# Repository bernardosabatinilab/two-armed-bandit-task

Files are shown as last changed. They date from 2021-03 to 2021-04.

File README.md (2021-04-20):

# two-armed-bandit-task

This is an experimental protcol designed within the Sabtini lab of a freely-moving two-armed-bandit task. These files will allow you to build the behavioral arena and begin running 2ABT in mice. 

Laser cutting plans to build the behavioral arena as well as 3D-printing files are located within the "laser cutter" folder. 
Printed Circuit Board (PCB) plans and code is available under the "Two-Armed-Bandit-PCB" repo forked from the Harvard Medical School Insrumentation Core https://github.com/bernardosabatinilab/Two-Armed-Bandit-PCB.
Aquisiton code to control the behavioral arena can be found in the "Mouse-Bandit-Behavior-markov" folder.

Please read "2ABT protocol" for details on behavioral training, learning criterion, and trouble shooting tips.

MATLAB and Arduino IDE is required.



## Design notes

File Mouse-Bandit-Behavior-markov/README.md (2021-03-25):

# two-armed-bandit-3PortNosePoke-behaviorCode
Code to run two-armed-bandit mouse behavior. Center port is initiation port, left and right ports are rewarded ports.

This code was developed by Shay Neufeld and Ofer Mazor

# Behavior Structure
Based on behavioral paradigm published in Tai & Lee et al. 2012 (http://www.ncbi.nlm.nih.gov/pmc/articles/PMC3951287/)

# What you need
Software Requirements:  
1. MATLAB (currently tested on 2015a and 2016a)  
2. Arduino (https://www.arduino.cc/en/Main/Software)  

Hardware Requirements:  
1. Arduino uno  
2. Custom circuit (please see Two-Armed-Bandit-PCB repo)  

Other materials:  
1. 3x IR beam detectors  
2. 3x nose ports  
3. box to contain mouse  
4. 3x LEDs  
5. Water delivery system (60ml syringe to hold water, various tubes, needle to deliver rewards, solenoids to drive water delivery).

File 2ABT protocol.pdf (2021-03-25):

Freely-Moving Two-Armed Bandit – Sabatini Lab
consolidated protocol from Lynne Chantranupong and Michael Wallace Habituation phase – 1 week prior to behavioral arena exposure
- Singly house mice, water deprived to 80% original body weight (BW)
- Handle mice for ~5 minutes/day
- Administer water by syringe during handling
- Place 1-1.5 mL of water in home cage to maintain water-restricted BW Pre-training/Daily setup – Configuring Arduino and data directory

### 1. Configure Arduino

a. Open Arduino IDE
b. Open MultiNoseportController
c. Compile and load onto Arduino board

### 2. Configure MATLAB

a. Add Mouse-Bandit-Behavior-markov folder to path
b. Run NewGUI in command window

### 3. Configure NewGUI – flush tubing

a. Select Connect to Arduino
b. Number of iterations = 100
c. Left/Right duration = 450 ms
d. Select Flush Left until all air bubbles are removed
e. Select Flush Right until all air bubbles are removed
f. Wipe away remaining water in ports

### 4. Running an experiment – choosing data directory

a. Define mouse name
b. Select: Choose Directory to Save In (select desired directory location)
c. Type in desired parameters in GUI
d. Select: Run Experiment

### 5. Stopping a session

a. Select: Stop Experiment
b. Clean box

Pre-training – behavioral arena setup/calibration
- Flush tubing with clean water by increasing solenoid valve opening time to 500 ms, 100 iterations on GUI.
- Change solenoid valve opening time to 50 ms, 1 iteration on GUI. Confirm that water delivery occurs in the form of a droplet.
- Calibrate ports (weekly) by:
1. Set solenoid opening time to 50 ms, 100 iterations
2. Aim for 300 uL of water to be dispensed during this time
3. Adjust solenoid opening time accordingly until both ports release 300 uL of water.

Training – 7-21 days
Day 1/Stage 1: Mice learn that water is available from side port lick spouts Bait center port and side ports with approximately 10 uL of water.
Weigh mouse then place in behavioral arena.
Set GUI parameters to:
Center poke trigger = 0
Center poke reward window = 0
Left/Right reward probability = 1/1
Min/Max block range: 1000
Learning criterion: train mice until they have reached a total of 150-200 rewarded trials then, proceed to next training stage.
Stage 2: Introduce trial structure – center to side nose poke for reward delivery
Bait lick spouts with 10 uL of water
Weigh mouse then place in behavioral arena
Session time = 40 min
Set GUI parameters to:
Center poke trigger: 15 s
Center poke reward window: 1
Left/Right reward probability: 1/1
Min/Max block range: 1000
Learning criterion: >100 correct trials/session; proceed to next training stage.
Stage 3: Learning block structure – rewarded trials switch sides with each block transition Bait center and rewarded ports with 10 uL of water.
Weigh mouse and place in behavioral arena.
Set GUI parameters to:
Center poke trigger: 15 s
Center poke reward window: 1
Left/Right reward probability: 1/0*
*Counterbalance rewarded side every session to minimize development of bias Min/Max block range: 30
Learning criterion: ~70% accuracy across 6 blocks; proceed to next training stage

Stage 4: Introduction of physical barrier between reward ports and initiation port

Note: A well-trained, experienced mouse can perform a single trial within 300-400 ms which is too fast to resolve a photometry signal for a single trial. Therefore, physical barriers are introduced to increase trial time.

Barriers reach a maximum length of 6 cm. These are introduced in a gradual, stepwise manner so that animals can adjust their movements to accommodate the barriers. Barriers begin at 1.5 cm in length then, increase to 3 cm then, finally to 6 cm.

Install appropriate barriers.
Bait center and rewarded ports with 10 uL of water.
*Note: Once mice achieve criterion on shortest barrier, stop baiting center port. Set GUI parameters to:
Center poke trigger: 15 s
Center poke reward window: 1
Left/Right reward probability: 1/0*
*Counterbalance rewarded side every session Min/Max block range: 30
Learning criterion: ~70% accuracy across 6 blocks then, can increase barrier length and/or move on to the final training stage.
Trouble shooting tips: If the mouse is struggling with the introduction of the barriers, change block range to 20 until mice perform well, bait rewarded port to help and place tape over unrewarded port if necessary. Then, increase block range to 30.

Stage 5: Final block structure for well-trained mice
Install longest barrier.
Bait rewarded ports with 10 uL of water.
Weigh mouse and place in behavioral arena.
Set GUI parameters to:
Center poke trigger: 5 s
Center poke reward window: 1 Left/Right reward probability: 0.9/0.1 Min/Max block range: 30

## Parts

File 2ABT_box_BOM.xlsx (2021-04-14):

Part | Type | Quantity | cost | total cost | Purpose | Notes | Link
noseport | box material | 3 |  | $0.00 | for poking | we can 3D-print these out here | see 3D printing files
#4-40 Cap screw | hardware | 1 | $10.00 | $10.00 | for box assembly | pre-thread holes for screws
Arduino UNO | hardware | 1 | $23.00 | $23.00 |  |  | https://www.arduino.cc/en/Main/ArduinoBoardUno
solenoid | electronics | 2 | $60.00 | $120.00 | for water delivery | LHQA0531220H (quiet click) | https://www.theleeco.com/products/electro-fluidic-systems/solenoid-valves/control-valves/lhq-series/3-port/ported/
LEDs | electronics | 3 | $10.00 | $30.00 | for lights |  | https://www.amazon.com/Emitting-Assortment-Diffused-Yellow-Colors/dp/B07DQQCXV9?hvadid=242051162351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
cables |  | 1 | $10.00 | $10.00 |  | Test Leads Breadboard 20 Pack 5.9 Inch (150mm) Wire Pin Contacts | http://www.jameco.com/webapp/wcs/stores/servlet/ProductDisplay?search_type=jamecoall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
IR beam detector | hardware | 3 | $6.46 | $19.38 | detect pokes |  | http://www.digikey.com/products/en?keywords=365-1769-ND
power source (5V) | electronics | 1 | $10.00 | $10.00 | for arduino |  | https://www.sparkfun.com/products/12889
Capacitive Touch Breakout | electronics | 3 | $6.00 | $18.00 | for lick detection |  | https://www.sparkfun.com/products/14520
60 mL syringes |  | 1 | $10.00 | $10.00 |  | water reservoir
tubing |  | 1 | $10.00 | $10.00 |  | Masterflex SC0040-LT Tygon E-Lab ext tubing, 1.42mm, 100ft | https://www.coleparmer.com/i/masterflex-sc0040-lt-tygon-e-lab-ext-tubing-1-42mm-100ft/0646034?searchterm=WU-06460-34
lick spouts |  | 1 | $10.00 | $10.00 |  |  | https://www.mcmaster.com/5560K72/
2AB printed circuit board | PCB | 1 |  | $0.00 |  | designed by Ofer Mazor, also includes parts list for screw terminals, ect. | https://github.com/HMS-RIC/Two-Armed-Bandit-PCB
Intel NUC NUC5i5RYK | computer | 1 | $1200.00 | $1200.00 | record data |  | https://www.amazon.com/Intel-NUC5i5RYK-Core-Processor-BOXNUC5I5RYK/dp/B00SD9ISIQ
Crucial 16GB Kit (8GBx2) DDR3-1600 MT/s (PC3-12800) 204-Pin SODIMM Notebook Memory CT2KIT102464BF160B / CT2CP102464BF160B | computer | 1 |  | $0.00 | record data |  | https://www.amazon.com/Crucial-DDR3-1600-PC3-12800-CT2KIT102464BF160B-CT2CP102464BF160B/dp/B007B5S52C
Samsung 850 EVO 500 GB M.2 3.5-Inch SSD (MZ-N5E500BW) | computer | 1 |  | $0.00 | record data |  | https://www.amazon.com/Samsung-850-EVO-3-5-Inch-MZ-N5E500BW/dp/B00TGIW1XG

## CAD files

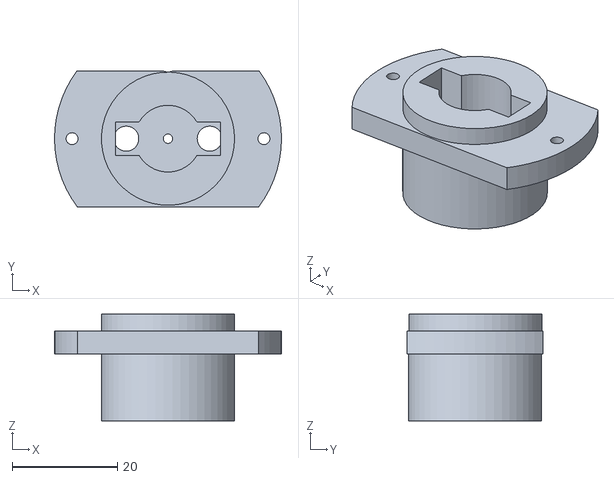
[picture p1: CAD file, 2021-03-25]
laser cutter/NosePokeBody.STL
43.2 x 25.8 x 20.3

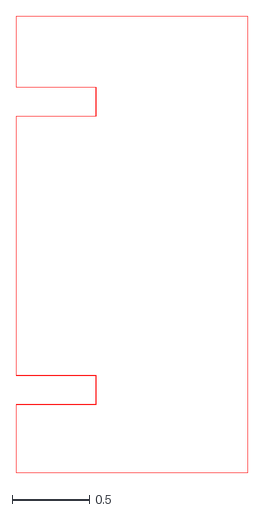
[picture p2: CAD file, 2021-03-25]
laser cutter/separation_holder.dxf
1.50 x 2.96

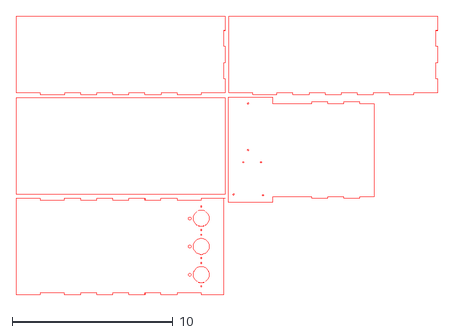
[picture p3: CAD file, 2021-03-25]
laser cutter/behavior box _small.dxf
26.2 x 17.3

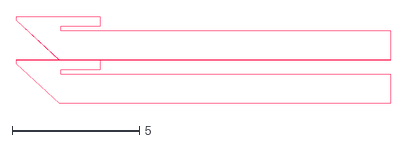
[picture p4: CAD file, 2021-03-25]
laser cutter/dividers_short.dxf
14.7 x 3.42

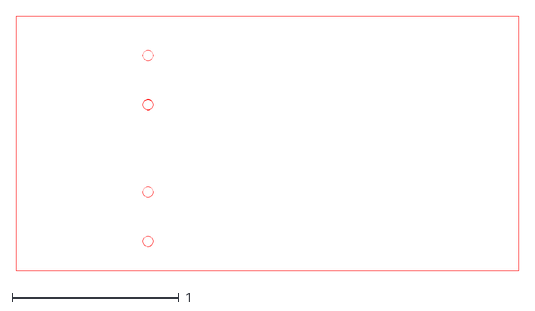
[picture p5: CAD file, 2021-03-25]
laser cutter/solinoid post.dxf
3.01 x 1.53

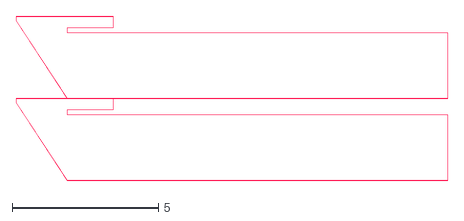
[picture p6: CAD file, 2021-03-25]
laser cutter/dividers_long.dxf
14.7 x 5.61

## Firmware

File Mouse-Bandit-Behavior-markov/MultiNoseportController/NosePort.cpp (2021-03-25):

#include "NosePort.h"
#include <Arduino.h>

extern void DEBUG(String message);

int NosePort::nosePortListSize = 0;
NosePort* NosePort::nosePortList[MAX_PORT_LIST_SIZE];

NosePort::NosePort(int beambreakPin, int solenoidPin) {
  _beambreakPin = beambreakPin;
  _solenoidPin = solenoidPin;
  _ledPin = 0;
  _rewardActivated = false;
  _rewardDuration_us = 0;
  _singleReward = false;

  _duringReward = 0;
  _rewardStartTime_us = 0;

  _laserPin = 0;
  _laserActivated = false;
  _laserStimDelay_us = 0;
  _laserStimDur_us = 0;
  _laserPulseDur_us = 0;
  _laserPulsePeriod_us = 0;

  _duringLaserStim = false;
  _laserStimStartTime_us = 0;
  _laserOn = false;

  pinMode(_beambreakPin, INPUT);
  _noseIn = (digitalRead(_beambreakPin) == HIGH);

  pinMode(_solenoidPin, OUTPUT);
  digitalWrite(_solenoidPin, LOW);

  if (nosePortListSize < MAX_PORT_LIST_SIZE-1) {
    nosePortList[nosePortListSize] = this;
    nosePortListSize += 1;
    _nosePortNumber = nosePortListSize; //nosePort number is ones-based
  } else {
    _nosePortNumber = 0;
  }

  logToUSB('N');

  DEBUG(String("New NosePort: ")+_nosePortNumber);
  DEBUG(String("- beam pin: ")+_beambreakPin);
  DEBUG(String("- sol pin: ")+_solenoidPin);

}

void NosePort::setRewardDuration(long duration) {
  DEBUG("Updated Duration");
  _rewardDuration_us = duration * 1000;
}

void NosePort::setActivated(bool activated) {
  DEBUG("Updated Activation State");
  _rewardActivated = activated;
}

void NosePort::setSingleReward(bool singleReward) {
  _singleReward = singleReward;
}

void NosePort::noseIn() {
  //DEBUG(String("Nose In — nosePort ")+_nosePortNumber);
  DEBUG(String("Nose In - nosePort ")+_nosePortNumber);
  _noseIn = true;
  // log noseIn
  logToUSB('I');
  if (_rewardActivated) {
    deliverReward();
  }
  if (_singleReward) {
    setActivated(false);
  }
  if (_laserActivated) {
    startLaserStim();
  }
}

void NosePort::noseOut() {
  DEBUG(String("Nose Out - nosePort ")+_nosePortNumber);
  _noseIn = false;
  // log noseOut
  logToUSB('O');
}

unsigned long pulseStartTime_us = 0;
void NosePort::update() {
  bool currentNosePortState = (digitalRead(_beambreakPin) == HIGH);
  if (_noseIn != currentNosePortState) { // if there's been a change in state
    if (currentNosePortState) {
      noseIn();
    } else {
      noseOut();
    }
  }
  if (_duringReward) {
    if (micros() - _rewardStartTime_us > _rewardDuration_us ) { // time comparison is corrected for overflow
      digitalWrite(_solenoidPin, LOW);
      _duringReward = false;
    }
  }
  if (_duringLaserStim) {
    // compute time since stim was triggered
    unsigned long stimTime = micros() - _laserStimStartTime_us;
    // check if we're still in the delay period
    if (stimTime > _laserStimDelay_us ) {
      // if we are past the delay, compute time since delay ended (i.e., time into pulsing)
      stimTime = stimTime - _laserStimDelay_us;
      if (stimTime >= _laserStimDur_us) {
        // if _laserStimDur is exceeded then end the stim
        endLaserStim();
      } else {
        // otherwise, turn laser on/off based on pulse parameters:
        if ((stimTime >= pulseStartTime_us) && (!_laserOn)) {
          digitalWrite(_laserPin, HIGH);
          _laserOn = true;          
        } else if ((stimTime >= pulseStartTime_us + _laserPulseDur_us) && (_laserOn)) {
          digitalWrite(_laserPin, LOW);
          _laserOn = false;
          pulseStartTime_us += _laserPulsePeriod_us;
        }
      }
    }
  }
}

void NosePort::deliverReward() {
  DEBUG(String("Reward - nosePort ") + _nosePortNumber);
  DEBUG(String("       - duration ") + (_rewardDuration_us / 1000));

  if (_rewardDuration_us > 0) {
    // set timer; set pin high; log
    _duringReward = true;
    _rewardStartTime_us = micros();
    digitalWrite(_solenoidPin, HIGH);
    logToUSB('R');

    // TODO Prevent rewards from overlapping; stop reward on nose out
  }
}


// LED methods
void NosePort::setLEDPin(int pin) {
  _ledPin = pin;
  pinMode(_ledPin, OUTPUT);
  digitalWrite(_ledPin, LOW);
}

void NosePort::ledOn() {
  if (_ledPin > 0) {
    digitalWrite(_ledPin, HIGH);
  }
}

void NosePort::ledOff() {
  if (_ledPin > 0) {
    digitalWrite(_ledPin, LOW);
  }
}

// Laser methods
void NosePort::setLaserPin(int pin) {
  _laserPin = pin;
  pinMode(_laserPin, OUTPUT);
  digitalWrite(_laserPin, LOW);}

void NosePort::setLaserDelay(long delay) {
  _laserStimDelay_us = delay * 1000;
}

void NosePort::setLaserStimDuration(long stimDur) {
  _laserStimDur_us = stimDur * 1000;
}

void NosePort::setLaserPulseDuration(long pulseDur) {
  _laserPulseDur_us = pulseDur * 1000;
}

void NosePort::setLaserPulsePeriod(long pulsePeriod) {
  _laserPulsePeriod_us = pulsePeriod * 1000;
}

void NosePort::setLaserActive(bool activated) {
  if (activated) {
    if (_laserPin > 0) {
      _laserActivated = true;
    }
  } else {
    _laserActivated = false;
  }
}

void NosePort::startLaserStim() {
  DEBUG(String("Laser Stim START - nosePort ")+_nosePortNumber);
  
  if (_laserPin > 0) {  
    _duringLaserStim = true;
    _laserStimStartTime_us = micros();  
    logToUSB('L'); 

    pulseStartTime_us = 0;
  }
}

void NosePort::endLaserStim() {
  DEBUG(String("Laser Stim END   - nosePort ")+_nosePortNumber);
  _duringLaserStim = false;
  digitalWrite(_laserPin, LOW);
  _laserOn = false;
  logToUSB('l'); 
}


// debug & logging methods
void NosePort::identify() {
  DEBUG(String("NosePort Num: ")+_nosePortNumber);
  DEBUG(String("- beam pin: ")+_beambreakPin);
  DEBUG(String("- sol pin: ")+_solenoidPin);
  DEBUG(String("- LED pin: ")+_ledPin);
}

void NosePort::logToUSB(char message) {
  String logMessgage = String(message);
  logMessgage += ' ';
  logMessgage += _nosePortNumber;
  Serial.println(logMessgage.c_str());
}


//===============

void NosePort::interpretCommand(String message) {
  message.trim(); // remove leading and trailing white space
  int len = message.length();
  if (len==0) {
    Serial.print("#"); // "#" means error
    return;
  }
  char command = message[0]; // the command is the first char of a message
  String parameters = message.substring(1);
  parameters.trim();

  String intString = "";
  while ((parameters.length() > 0) && (isDigit(parameters[0]))) {
    intString += parameters[0];
    parameters.remove(0,1);
  }
  unsigned long arg1 = intString.toInt();

  parameters.trim();
  intString = "";
  while ((parameters.length() > 0) && (isDigit(parameters[0]))) {
    intString += parameters[0];
    parameters.remove(0,1);
  }
  unsigned long arg2 = intString.toInt();


  DEBUG(String("Command: ")+command);
  DEBUG(String("Argument 1: ")+arg1);
  DEBUG(String("Argument 2: ")+arg2);

  if (command == 'N') { // N: new nosePort
    // arg1 is beambreak pin
    // arg2 is solenoid pin
    new NosePort(arg1, arg2);
  } else {

    if ((arg1 <= 0) || (arg1 > nosePortListSize)) {
      // Bad NosePort Number
      Serial.print("#"); // "#" means error
      return;
    }
    int nosePortNum = arg1;

    if (command == 'D') { // D: set reward duration
      nosePortList[nosePortNum-1]->setRewardDuration(arg2);
    } else if (command == 'A') { // A: set reward activation state
      nosePortList[nosePortNum-1]->setActivated(arg2);
    } else if (command == 'S') { // S: set single-reward state
      nosePortList[nosePortNum-1]->setSingleReward(arg2);
    } else if (command == 'R') { // R: deliver reward
      nosePortList[nosePortNum-1]->deliverReward();

    } else if (command == 'L') { // L: set LED pin
      nosePortList[nosePortNum-1]->setLEDPin(arg2);
    } else if (command == 'O') { // L: turn LED on
      nosePortList[nosePortNum-1]->ledOn();
    } else if (command == 'F') { // L: turn LED off
      nosePortList[nosePortNum-1]->ledOff();

    } else if (command == 'P') { // P: set laser pin
      nosePortList[nosePortNum-1]->setLaserPin(arg2);
    } else if (command == 'Y') { // Y: set laser delay
      nosePortList[nosePortNum-1]->setLaserDelay(arg2);
    } else if (command == 'T') { // T: set laser stim duration
      nosePortList[nosePortNum-1]->setLaserStimDuration(arg2);
    } else if (command == 'U') { // U: set laser pulse duration
      nosePortList[nosePortNum-1]->setLaserPulseDuration(arg2);
    } else if (command == 'I') { // I: set laser pulse period
      nosePortList[nosePortNum-1]->setLaserPulsePeriod(arg2);
    } else if (command == 'V') { // V: set laser activation state
      nosePortList[nosePortNum-1]->setLaserActive(arg2);

    } else { // unknown command
      Serial.print("#"); // "#" means error
    }
  }
}

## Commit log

2021-03-25 Create laser cutter plans
2021-03-25 Rename behavior box _large.dxf to laser cutter/behavior box _large.dxf
    [behavior box _large.dxf]
2021-03-25 Rename behavior box _small.dxf to laser cutter/behavior box _small.dxf
    [behavior box _small.dxf]
2021-03-25 Rename dividers_long.dxf to laser cutter/dividers_long.dxf
    [dividers_long.dxf]
2021-03-25 Rename dividers_short.dxf to laser cutter/dividers_short.dxf
    [dividers_short.dxf]
2021-03-25 Rename separation_holder.dxf to laser cutter/separation_holder.dxf
    [separation_holder.dxf]
2021-03-25 Rename solinoid post.dxf to laser cutter/solinoid post.dxf
    [solinoid post.dxf]
